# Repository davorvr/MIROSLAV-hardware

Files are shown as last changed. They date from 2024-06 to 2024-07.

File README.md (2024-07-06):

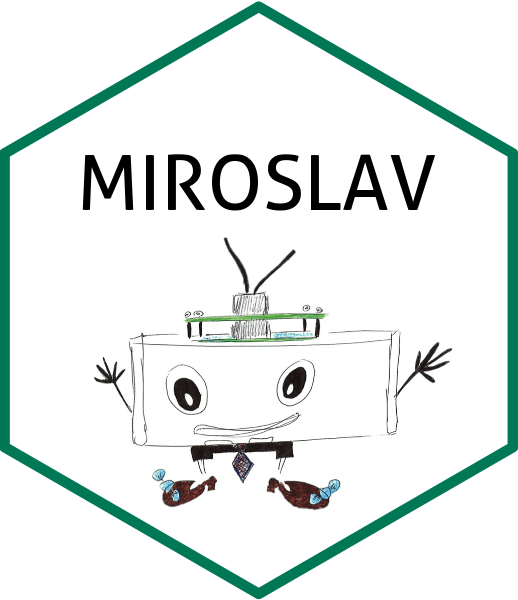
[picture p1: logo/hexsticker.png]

<br> MIROSLAV hardware <br>
  <br clear="left"/>
========

### What is it?

This repo holds everything needed to build a working MIROSLAV device. Arduino firmware and Record-a-SLAV, a Python data acquisition script, can be found in the [`MIROSLAV-firmware` repository](https://github.com/davorvr/MIROSLAV-firmware). A complete, user-friendly MIROSLAV software toolkit for analysis of MIROSLAV data, from raw data to statistical analysis, can be found in the [`MIROSLAV-analysis` repository](https://github.com/davorvr/MIROSLAV-analysis) - also contains an example dataset of real data recorded in our lab.

### What is MIROSLAV, anyway?

**MIROSLAV (_Multicage InfraRed Open Source Locomotor Activity eValuator_)** is a platform for non-invasive monitoring of circadian locomotor activity in laboratory rodents. MIROSLAV is fully open source and scalable to hundreds of cages. All of its hardware and software components are described in the paper: https://doi.org/10.1101/2024.06.25.600592

***

### File tree

- `bom/` - Bill of Materials for all needed parts and an informative order sheet for the PCBs. Note that the PCBs are panelised so e.g. 10 pcs of the sensor board refer to 10x2 panels - total 200 boards.

- `gerbers/` - Last produced gerber files - MIROSLAV v0.4, as described in the paper

- KiCad board project directories:
  - `main_board/`
  - `power_board/`
  - `sensor_board/`
  - `serialization_board/`

- `symbols/` - Contains additional individual symbols and footprints used.

- `miro-v04.pretty/` - Contains additional symbols, packed into a `.pretty` library (footprints)

- `miro-v04.kicad_sym` - Contains additional symbols, packed into a `.kicad_sym` library (schematic symbols)

### About the current state of the designs

MIROSLAV's current hardware revision is **v0.4**, designed in Dec 2021 in KiCad 6.0. At that time, we generated Gerbers and produced the PCBs through JLCPCB. The devices have been successfully in the proof-of-concept study described in the paper.

The only change made in the meantime was a verbatim conversion of project files to KiCad 8.0 format for convenience of further development. Original Gerber files still remain so that a tested MIROSLAV design can be easily reproduced.

Note the **[v0.5 branch](https://github.com/davorvr/MIROSLAV-hardware/tree/v0.5)** which contains updated designs that haven't been produced/tested yet.

**To reproduce MIROSLAV, it is sufficient to download the Gerbers and send them to a PCB manufacturer.**

Additional part symbols and footprints used in the design are contained in `miro-v04.kicad_sym` and `miro-v04.pretty` libraries, respectively.

### Related repositories

* [`MIROSLAV-firmware`](https://github.com/davorvr/MIROSLAV-firmware) - Arduino firmware and Record-a-SLAV, a Python data acquisition script. Once you build the device, you need to flash the firmware, set up an MQTT broker, and run Record-a-SLAV on a PC to start recording data.
* [`mirofile`](https://github.com/davorvr/mirofile) - Your buddy for dealing with raw MIROSLAV data. A Python library used by Prepare-a-SLAV to parse raw MIROSLAV logs into a dataframe.
* [`MIROSLAV-analysis`](https://github.com/davorvr/MIROSLAV-analysis) - A complete, user-friendly MIROSLAV software toolkit for analysis of MIROSLAV data, from raw data to statistical analysis. Also contains an example dataset with real data recorded in our lab.

### License

You can modify any part of MIROSLAV freely under the **GPLv3** license - if you have any questions, problems, or ideas on how to improve MIROSLAV, feel free to reach out to us, submit a GitHub issue, or a pull request.

The MIROSLAV logo is created by Petra Šoštarić Mužić and licensed under the **CC BY-NC-SA 4.0** license - more details can be found in the repository's [`logo/` directory](logo/).

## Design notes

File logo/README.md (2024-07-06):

# MIROSLAV logo

Drawn by: **Petra Šoštarić Mužić**

The adjusted version makes parts of the background transparent and shortens the cables to fit into a hexagon. The hexagonal sticker used as the MIROSLAV logo was made using the [`hexSticker`](https://cran.r-project.org/web/packages/hexSticker/index.html) package.

Images in this directory (the drawing, its variations, and the hexagonal logo) are licensed under the [Creative Commons Attribution-NonCommercial-ShareAlike 4.0 International License][cc-by-nc-sa].

[][cc-by-nc-sa]

[cc-by-nc-sa]: http://creativecommons.org/licenses/by-nc-sa/4.0/
[cc-by-nc-sa-image]: https://licensebuttons.net/l/by-nc-sa/4.0/88x31.png
[cc-by-nc-sa-shield]: https://img.shields.io/badge/License-CC%20BY--NC--SA%204.0-lightgrey.svg

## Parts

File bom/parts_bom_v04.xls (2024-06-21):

FULLBOM_MIROSLAV_V0.4 | Project URL: | https://www.mouser.com/ProjectManager/ProjectDetail.aspx?AccessID=c61e05c8b2
Mouser No | Mfr. No | Manufacturer | Customer No | Description | RoHS | Lifecycle | Order Qty. | Price (EUR) | Ext.: (EUR)
530-937-SP-3044 | 937-SP-3044 | Bel |  | Modular Connectors / Ethernet Connectors RJ9 Connector 4 Pins 4 Condutors | RoHS Compliant |  | 300 | 0.136 € | 40.80 €
649-61835-0441LF | 61835-0441LF | Amphenol |  | Modular Connectors / Ethernet Connectors 4-4 VERT PCB JACK | RoHS Compliant |  | 150 | 0.399 € | 59.85 €
571-440055-2 | 440055-2 | TE Connectivity |  | Headers & Wire Housings 2.0mm HDR 2pos R/A HPI | RoHS Compliant |  | 500 | 0.089 € | 44.50 €
571-440129-4 | 440129-4 | TE Connectivity |  | Headers & Wire Housings 4 POS RECPT 2.0mm | RoHS Compliant |  | 100 | 0.100 € | 10.00 €
571-440129-2 | 440129-2 | TE Connectivity |  | Headers & Wire Housings 2.0mm RCPT 2pos HPI | RoHS Compliant |  | 500 | 0.030 € | 15.00 €
571-1735446-4 | 1735446-4 | TE Connectivity |  | Headers & Wire Housings 4 POS HDR VERT 2.0mm | RoHS Compliant |  | 100 | 0.112 € | 11.20 €
517-C3801/40 | C3801/40 | 3M |  | Flat Cables RND CND FLT 26G PVC CAN.CERT 40CND .5" | RoHS Compliant |  | 1 | 115.360 € | 115.36 €
418-30RDM5011G02BKBV | TR30RDM050-11G02-BK-BK VI | Cincon |  | Wall Mount AC Adapters |  |  | 5 | 18.930 € | 94.65 €
855-M20-9990245 | M20-9990245 | Harwin |  | Headers & Wire Housings 02 SIL VERTICAL PIN HEADER GOLD HT | RoHS Compliant |  | 30 | 0.137 € | 4.11 €
855-M20-9990445 | M20-9990445 | Harwin |  | Headers & Wire Housings 04 SIL VERTICAL PIN HEADER GOLD HT | RoHS Compliant |  | 30 | 0.196 € | 5.88 €
855-M20-7820442 | M20-7820442 | Harwin |  | Headers & Wire Housings 4 PIN SIL VERTICAL SOCKET GOLD+TIN | RoHS Compliant |  | 30 | 0.773 € | 23.19 €
855-M20-7820242 | M20-7820242 | Harwin |  | Headers & Wire Housings 2 PIN SIL VERTICAL SOCKET GOLD+TIN | RoHS Compliant |  | 30 | 0.685 € | 20.55 €
855-M20-7820342 | M20-7820342 | Harwin |  | Headers & Wire Housings 3 PIN SIL VERTICAL SOCKET GOLD+TIN | RoHS Compliant |  | 300 | 0.639 € | 191.70 €
855-R30-3011102 | R30-3011102 | Harwin |  | Standoffs & Spacers M3 x 11mm HEX 5mmA/F 8mm ML/FML NICKEL | RoHS Compliant By Exemption |  | 100 | 0.252 € | 25.20 €
571-1735801-1 | 1735801-1 | TE Connectivity |  | Headers & Wire Housings 2mm CRMP SCKT 24-30 AWG Reel of 10000 | RoHS Compliant |  | 10000 | 0.009 € | 90.00 €
356-ESP32-S2-SAOLA-R | ESP32-S2-Saola-1R | Espressif |  | WiFi Development Tools - 802.11 ESP32-S2 general-purpose development board, embeds ESP32-S2-WROVER, 4 MB flash, with pin header | RoHS Compliant | End of Life | 6 | 7.440 € | 44.64 €
71-CRCW1206-1.0K-E3 | CRCW12061K00FKEA | Vishay |  | Thick Film Resistors - SMD 1/4watt 1.0Kohms 1% | RoHS Compliant By Exemption |  | 100 | 0.018 € | 1.80 €
80-C1206C104J5RACTU | C1206C104J5RAC7800 | KEMET |  | Multilayer Ceramic Capacitors MLCC - SMD/SMT 50V 0.1uF X7R 1206 5% | RoHS Compliant |  | 100 | 0.042 € | 4.20 €
579-MCP23017-E/SP | MCP23017-E/SP | Microchip |  | Interface - I/O Expanders 16bit Input/Output Exp I2C interface | RoHS Compliant |  | 30 | 1.300 € | 39.00 €
Funduino | Store URL: | https://funduinoshop.com/en
Item no. | Item |  |  | URL |  |  | Qty. | Price (EUR) | Ext.: (EUR)
FUN-1010565 | Motion detector, PIR sensor - HC-SR501 |  |  | https://funduinoshop.com/en/electronic-modules/sensors/movement-distance/motion-detector-pir-sensor-hc-sr501 |  |  | 130 | 1.97 € | 255.63 €
F23106532 | GY 213V HDC1080 temperature and humidity sensor |  |  | https://funduinoshop.com/en/electronic-modules/sensors/temperature/gy-213v-hdc1080-temperature-and-humidity-sensor |  |  | 6 | 4.66 € | 27.98 €
BerryBase | Store URL: | https://www.berrybase.de/en/
Item no. | Item |  |  | URL |  |  | Qty. | Price (EUR) | Ext.: (EUR)
GY-302; 4251266702504 | BH1750 Digitaler Lichtsensor |  |  | https://www.berrybase.de/en/bh1750-digitaler-lichtsensor |  |  | 6 | 2.02 € | 12.10 €
 |  |  |  |  |  | Total, parts (EUR, excl. VAT) |  |  | 1137.34 €
 |  |  |  |  | ESTIMATES! (depends on region) | Total, incl. PCBs (EUR, excl. VAT & shipping) |  |  | 1405.34 €
 |  |  |  |  |  | Total (EUR, incl. 19% VAT & shipping) |  |  | 1499.33 €

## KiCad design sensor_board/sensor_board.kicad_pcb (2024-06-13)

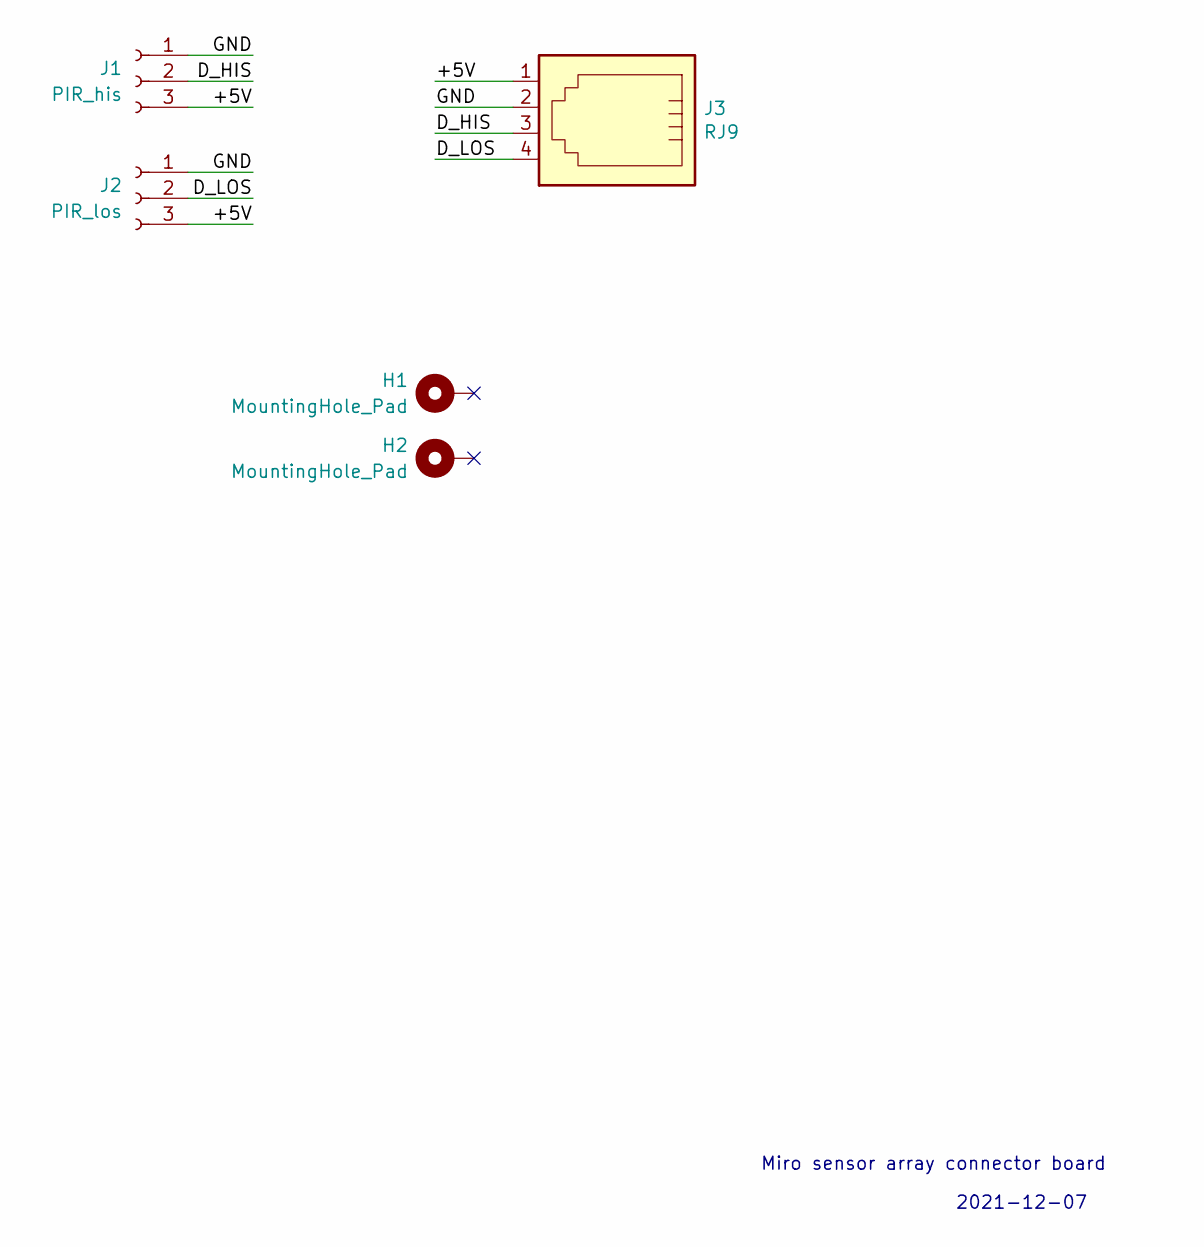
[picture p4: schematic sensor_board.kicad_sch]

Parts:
H1: MountingHole_Pad; MountingHole_4.3mm_M4_ISO14580_Pad
H2: MountingHole_Pad; MountingHole_4.3mm_M4_ISO14580_Pad_OVAL
J1: PIR_his; PinSocket_1x03_P2.54mm_Vertical
J2: PIR_los; PinSocket_1x03_P2.54mm_Vertical
J3: RJ9; 4P4C_RJ9_vert

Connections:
/+5V: J1.3, J2.3, J3.1
/D_HIS: J1.2, J3.3
/D_LOS: J2.2, J3.4
/GND: J1.1, J2.1, J3.2

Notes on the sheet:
Miro sensor array connector board
2021-12-07

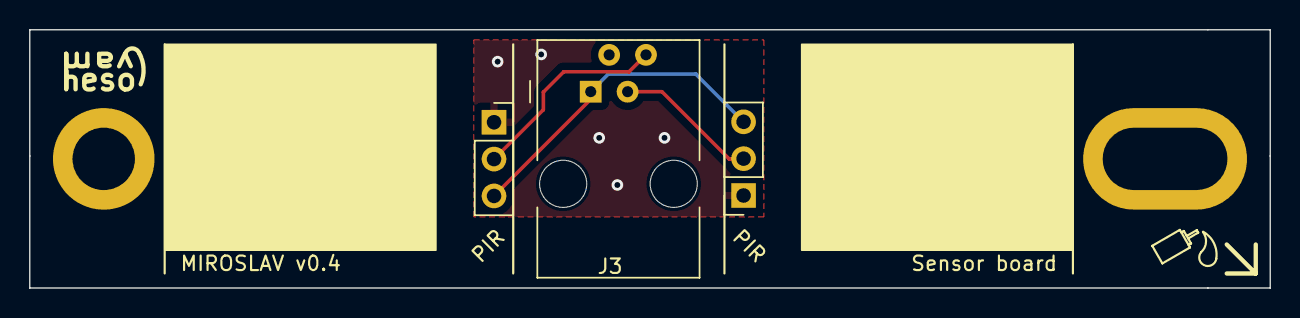
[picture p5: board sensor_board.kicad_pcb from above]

Board: 2 copper layers, 85.5 x 17.8 mm, 5 parts (0 on the bottom side), 4 nets.

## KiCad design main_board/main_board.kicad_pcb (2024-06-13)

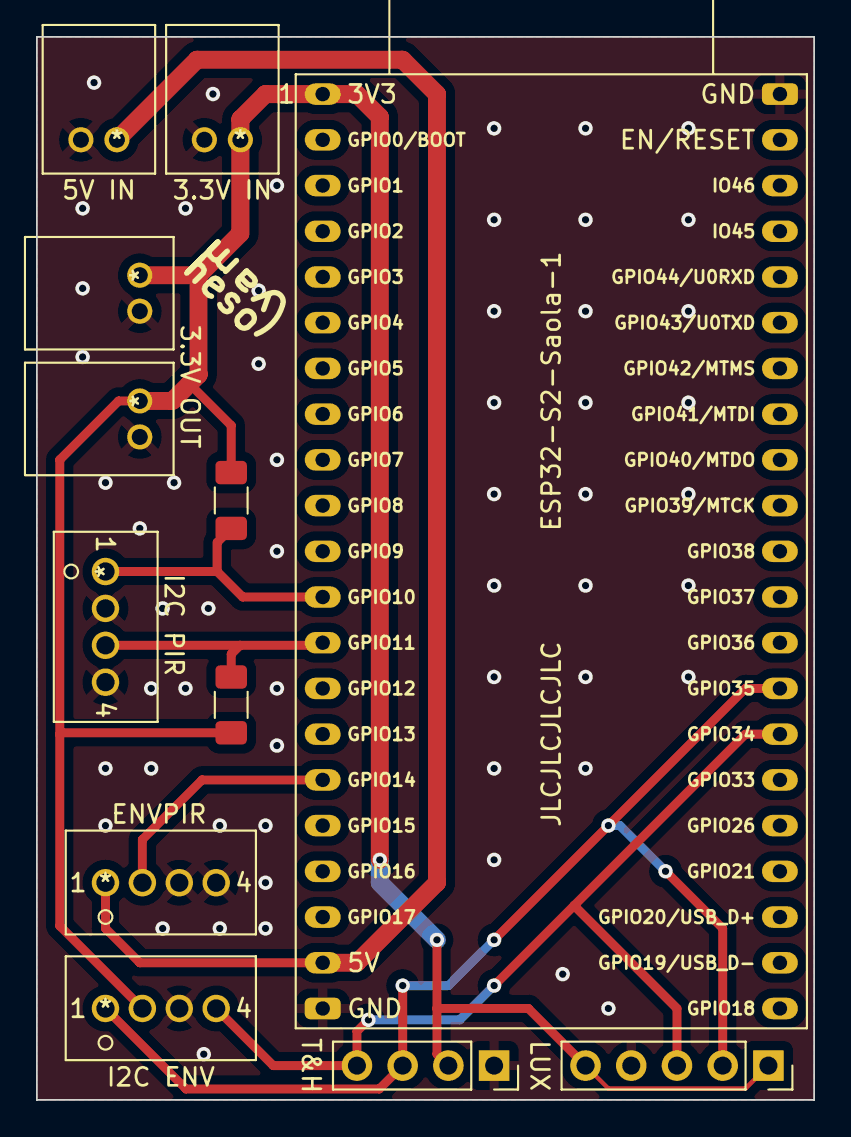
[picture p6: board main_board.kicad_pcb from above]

Board: 2 copper layers, 43.2 x 59.1 mm, 12 parts (0 on the bottom side), 8 nets.

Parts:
J1: 5V IN; TE_HDI_2_horiz
J2: 3.3V IN; TE_HDI_2_horiz
J3: I2C PIR; TE_HDI_4_vert
J4, J5: 3.3V OUT; TE_HDI_2_horiz
J12: I2C ENV; TE_HDI_4_vert
J13: ENVPIR; TE_HDI_4_vert
LUX: BH1750 (lux); PinSocket_1x05_P2.54mm_Vertical
R1, R2: 1k; R_1206_3216Metric_Pad1.30x1.75mm_HandSolder
T&H: HDC1080 (temp&hum); PinSocket_1x04_P2.54mm_Vertical
U1: ESP32-S2-Saola-1

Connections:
+3V3: J2.1, J4.1, J5.1, J12.2, LUX.1, LUX.5, R1.2, R2.1, T&H.2, U1.1
+5V: J1.1, J13.1, U1.20
/ENVPIR_DIN: J13.2, U1.16
/ENV_SCL: J12.4, LUX.3, T&H.4, U1.28
/ENV_SDA: J12.1, LUX.2, T&H.3, U1.29
/PIR_SCL: J3.3, R1.1, U1.13
/PIR_SDA: J3.1, R2.2, U1.12
GND: J1.2, J2.2, J3.2, J3.4, J4.2, J5.2, J12.3, J13.3, J13.4, LUX.4, T&H.1, U1.21, U1.42

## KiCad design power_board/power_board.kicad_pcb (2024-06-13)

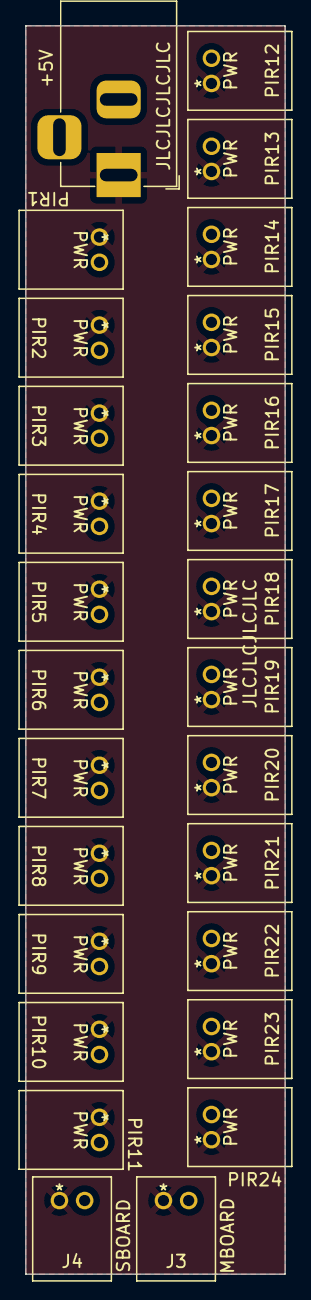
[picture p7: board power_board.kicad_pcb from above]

Board: 2 copper layers, 20.6 x 99.1 mm, 27 parts (0 on the bottom side), 2 nets, no tracks yet.

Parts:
+5V: PWR IN; BarrelJack_Horizontal
J3: MBOARD; TE_HDI_2_horiz_altsilk
J4: SBOARD; TE_HDI_2_horiz_altsilk
PIR1, PIR2, PIR3, PIR4, PIR5, PIR6, PIR7, PIR8, PIR9, PIR10, PIR11, PIR12, PIR13, PIR14, PIR15, PIR16, PIR17, PIR18, PIR19, PIR20, PIR21, PIR22, PIR23, PIR24: PWR; TE_HDI_2_horiz_altsilk

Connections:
+5V: +5V.1, J3.1, J4.1, PIR1.1, PIR2.1, PIR3.1, PIR4.1, PIR5.1, PIR6.1, PIR7.1, PIR8.1, PIR9.1, PIR10.1, PIR11.1, PIR12.1, PIR13.1, PIR14.1, PIR15.1, PIR16.1, PIR17.1, PIR18.1, PIR19.1, PIR20.1, PIR21.1, PIR22.1, PIR23.1, PIR24.1
GND: +5V.2, +5V.3, J3.2, J4.2, PIR1.2, PIR2.2, PIR3.2, PIR4.2, PIR5.2, PIR6.2, PIR7.2, PIR8.2, PIR9.2, PIR10.2, PIR11.2, PIR12.2, PIR13.2, PIR14.2, PIR15.2, PIR16.2, PIR17.2, PIR18.2, PIR19.2, PIR20.2, PIR21.2, PIR22.2, PIR23.2, PIR24.2

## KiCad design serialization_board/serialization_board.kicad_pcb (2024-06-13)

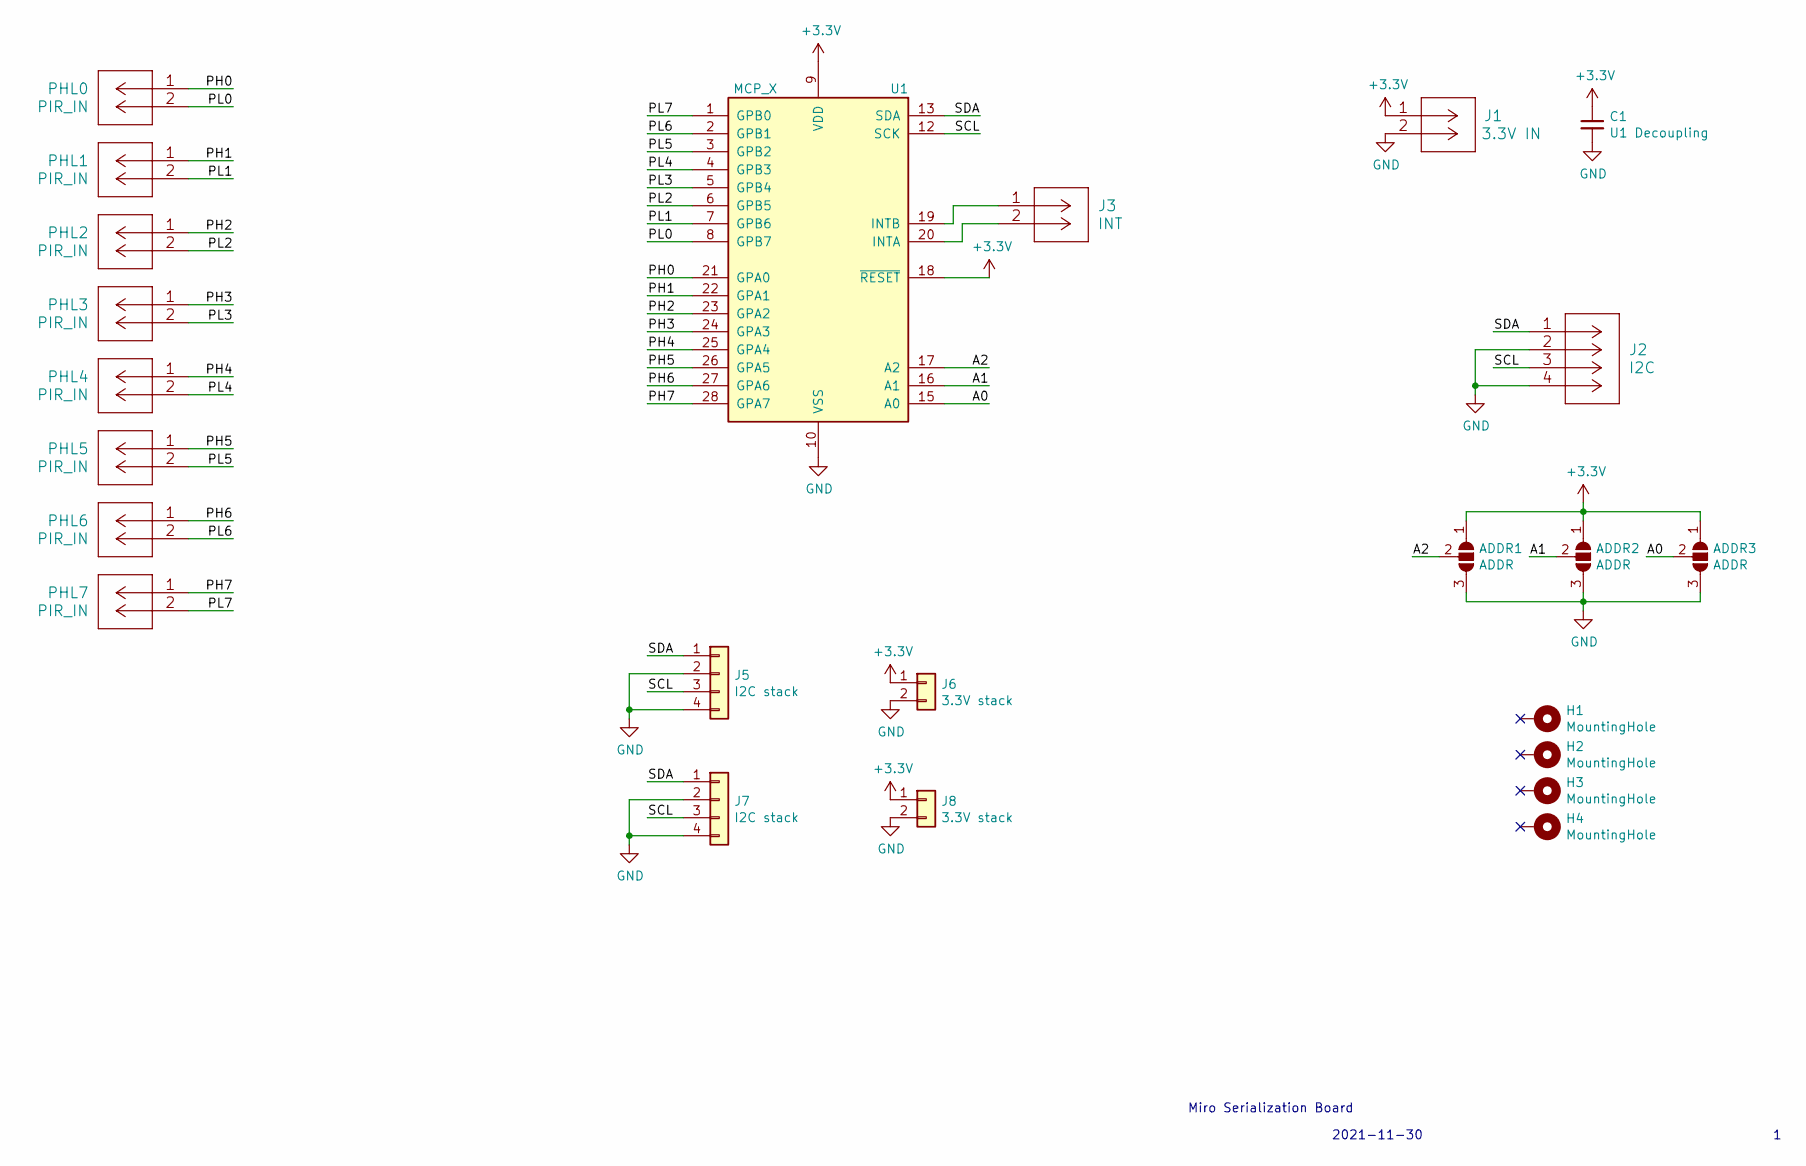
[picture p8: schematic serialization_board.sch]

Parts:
ADDR1, ADDR2, ADDR3: ADDR; SolderJumper-3_P1.3mm_Open_Pad1.0x1.5mm_NumberLabels
C1: U1 Decoupling; C_1206_3216Metric_Pad1.33x1.80mm_HandSolder
H1, H2, H3, H4: MountingHole; MountingHole_4.3mm_M4_ISO14580_Pad
J1: 3.3V IN; TE_HDI_2_horiz
J2: I2C; TE_HDI_4_vert
J3: INT; TE_HDI_2_horiz
J5: I2C stack; PinSocket_1x04_P2.54mm_Vertical
J6: 3.3V stack; PinSocket_1x02_P2.54mm_Vertical
J7: I2C stack; PinHeader_1x04_P2.54mm_Vertical
J8: 3.3V stack; PinHeader_1x02_P2.54mm_Vertical
PHL0, PHL1, PHL2, PHL3, PHL4, PHL5, PHL6, PHL7: PIR_IN; TE_HDI_2_horiz
U1: MCP_X; DIP-28_W7.62mm

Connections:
+3V3: ADDR1.1 (A), ADDR2.1 (A), ADDR3.1 (A), C1.1, J1.1, J6.1, J8.1, U1.9 (VDD), U1.18 (~RESET~); also elsewhere on the board
/A0: ADDR3.2 (C), U1.15 (A0)
/A1: ADDR2.2 (C), U1.16 (A1)
/A2: ADDR1.2 (C), U1.17 (A2)
/PH0: PHL0.1, U1.21 (GPA0)
/PH1: PHL1.1, U1.22 (GPA1)
/PH2: PHL2.1, U1.23 (GPA2)
/PH3: PHL3.1, U1.24 (GPA3)
/PH4: PHL4.1, U1.25 (GPA4)
/PH5: PHL5.1, U1.26 (GPA5)
/PH6: PHL6.1, U1.27 (GPA6)
/PH7: PHL7.1, U1.28 (GPA7)
/PL0: PHL0.2, U1.8 (GPB7)
/PL1: PHL1.2, U1.7 (GPB6)
/PL2: PHL2.2, U1.6 (GPB5)
/PL3: PHL3.2, U1.5 (GPB4)
/PL4: PHL4.2, U1.4 (GPB3)
/PL5: PHL5.2, U1.3 (GPB2)
/PL6: PHL6.2, U1.2 (GPB1)
/PL7: PHL7.2, U1.1 (GPB0)
/SCL: J2.3, J5.3, J7.3, U1.12 (SCK); also elsewhere on the board
/SDA: J2.1, J5.1, J7.1, U1.13 (SDA); also elsewhere on the board
GND: ADDR1.3 (B), ADDR2.3 (B), ADDR3.3 (B), C1.2, J1.2, J2.2, J2.4, J5.2, J5.4, J6.2, J7.2, J7.4, J8.2, U1.10 (VSS); also elsewhere on the board
unnamed: J3.1, U1.19 (INTB)
unnamed: J3.2, U1.20 (INTA)

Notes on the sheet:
Miro Serialization Board
2021-11-30

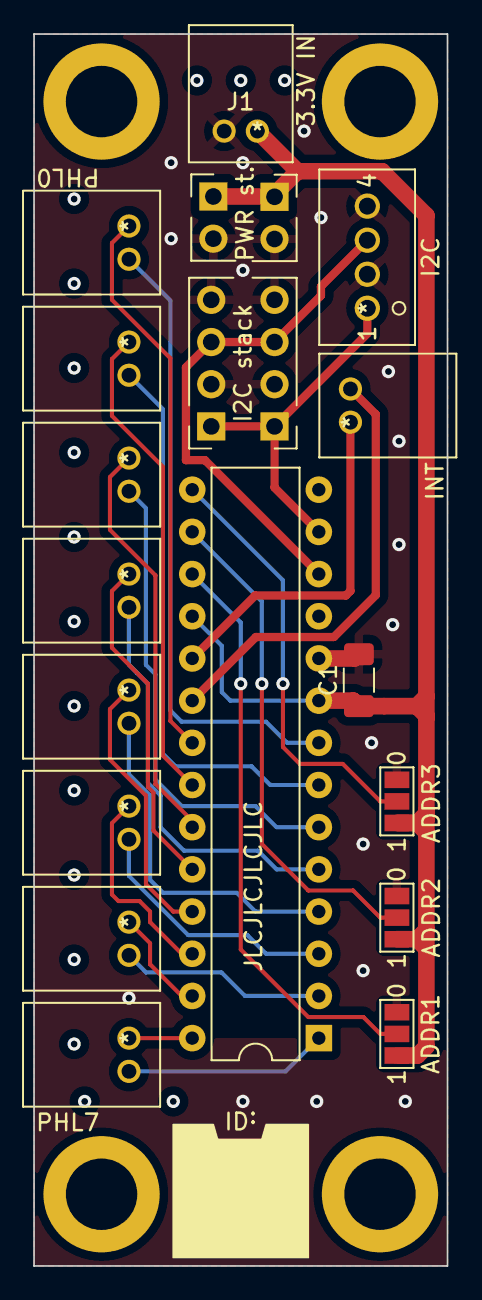
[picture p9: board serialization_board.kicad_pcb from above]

Board: 2 copper layers, 24.9 x 74.2 mm, 24 parts (0 on the bottom side), 25 nets.

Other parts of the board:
I2C stack: I2C stack; PinSocket_1x04_P2.54mm_Vertical
PWR st.: 3.3V stack; PinHeader_1x02_P2.54mm_Vertical

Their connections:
+3V3: PWR st..1; also elsewhere on the board
/SCL: I2C stack.3; also elsewhere on the board
/SDA: I2C stack.1; also elsewhere on the board
GND: I2C stack.2, I2C stack.4, PWR st..2; also elsewhere on the board

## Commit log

2024-06-19 Added BOM and updated README
    [parts_bom_v04.xls]
2024-06-20 Specified decoupling cap value
    [serialization_board.kicad_sch]
2024-06-20 Added SMD parts to BOM
    [parts_bom_v04.xls]
2024-06-20 Fixed BOM
    [parts_bom_v04.xls]

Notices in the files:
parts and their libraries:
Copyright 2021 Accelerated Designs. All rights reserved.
